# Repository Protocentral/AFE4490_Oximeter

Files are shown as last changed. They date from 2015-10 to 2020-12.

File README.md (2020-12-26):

ProtoCentral AF4490-based Pulse-oximeter shield for Arduino
================================
[Dont have it yet? Buy one here: ProtoCentral AFE4490 Pulse Oximeter Shield for Arduino – v2 (PC-MED-0406)](https://protocentral.com/product/protocentral-afe4490-pulse-oximeter-shield-for-arduino-v2/)
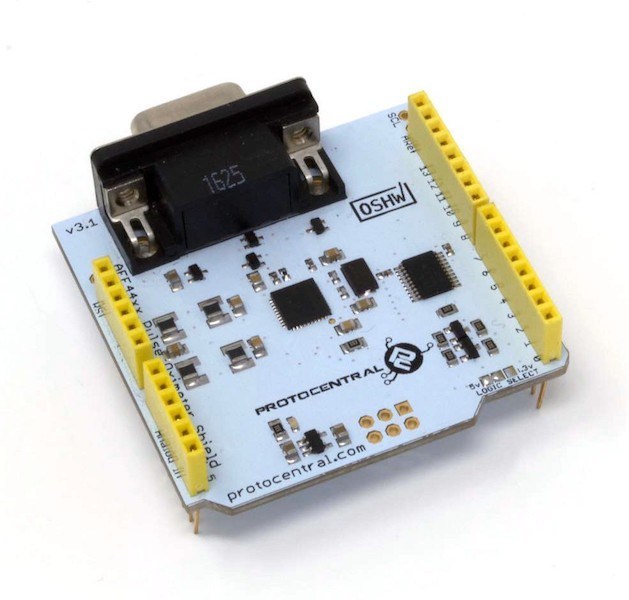
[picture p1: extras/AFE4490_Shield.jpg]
Pulse Oximeter Shield


[Dont have it yet? Buy one here: ProtoCentral AFE4490 Pulse Oximeter Breakout Board Kit (PC-MED-0405)](https://protocentral.com/product/protocentral-afe4490-pulse-oximeter-breakout-board-kit/)
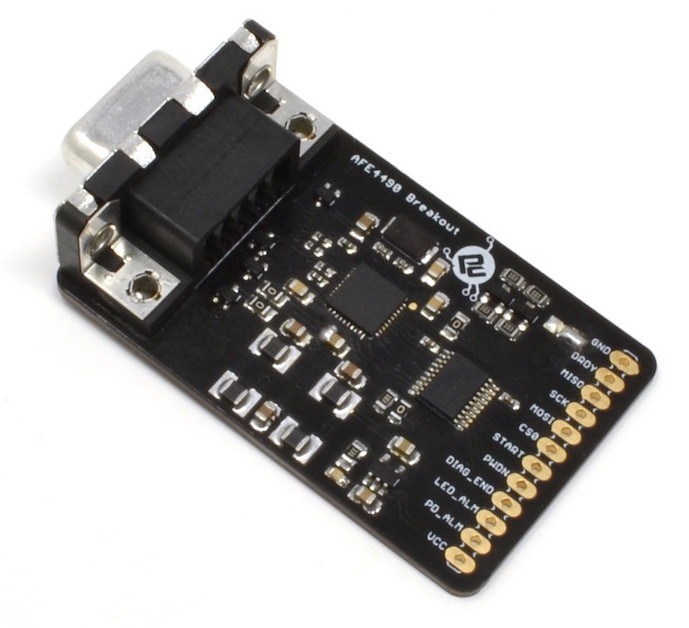
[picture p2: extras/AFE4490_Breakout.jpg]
Pulse Oximeter Breakout


### If you're looking for the Arduino library, it's now moved here: https://github.com/Protocentral/protocentral-afe4490-arduino

This pulse oximetry shield from ProtoCentral uses the AFE4490 IC to enble your Arduino to measure heart rate as well as SpO2 values.
Pulse oximetry is an indirect method of measuring the oxygen levels in the blood. The sensor measures the skin's absorbance of red and IR light wavelengths to calculate the oxygen levels. The measurement is done by a probe that clips on to a finger and contains emitters as well as a light sensor.
Since the amount of blood flowing through any blood vessel varies (pulses) with the rate of blood from the heart, this can also be used for measuring heartrate without the need for connecting any ECG electrodes. 
Used along with Brainbay, this shield can display the real-time PPG as well as heart-rate values in addition to SpO2.

Features:
* TI AFE4490 Single chip pulse pulsoximetry front-end IC
* Standard Nellcor compatible DB7 connector for probe
* Calculates Spo2 values with provided code
* Real-time display of PPG (Photoplethysmogram)

## Includes:
----------
* 1x ProtoCentral Pulse Oximetry shield for Arduino
* 1x Set of stackable Arduino headers
* 1x "Nellcor compatible" Pulse oximetry finger probe. 

## Repository Contents
-------------------
* **/arduino** - Arduino library and example sketch
* **/hardware** - All Eagle design files (.brd, .sch)
* **/extras** - datasheets and extras
* **/processing** - Processing-based Application

## Connecting the shield to your Arduino
-------------------------------------
 Connect the ECG/Respiration shield to the Arduino by stacking it on top of your Arduino. This shield uses the SPI interface  to communicate with the Arduino. Since this includes the ICSP header, which is used on newer Arduinos for SPI communication,  this shield is also compatible newer Arduino boards such as the Arduino Yun and Due.

## The Arduino library for this is now available here: https://github.com/Protocentral/protocentral-afe4490-arduino

## Wiring the Breakout to your Arduino
------------------------------------
 If you have bought the breakout the connection with the Arduino board is as follows:
 
|AFE4490 pin label| Arduino Connection   |Pin Function                  |
|----------------- |:--------------------:|-----------------:           |
| GND              | Gnd                  |  Gnd                        |             
| DRDY             | D2                   |  Data ready(interrupt)      |
| MISO             | D12                  |  Slave out                  |
| SCK              | D13                  |  SPI clock                  |
| MOSI             | D11                  |  Slave in                   |
| CS0              | D7                   |  Slave select               |
| START            | D5                   |  Conversion start Pin       |
| PWDN             | D4                   |  Power Down/ Reset          |
| DIAG_END         | NC                   |  Diagnostic output          |
| LED_ALM          | NC                   |  Cable fault indicator      |
| PD_ALM           | NC                   |  PD sensor fault indicator  |
| VCC              | +5v                  |  Supply voltage             |

## Using Processing - Data Visualization Software
----------------------------------------------
 Processing is a data visualization software, in existence since 2001, used by artists and scientists alike. It’s an open source coding framework based on Java. If you are familiar with the Arduino environment, the Processing IDE is similar and you won’t have much of a learning curve to climb!
 
 The following are the steps to run the code:

### 1. Download and Install Processing 

 Download the processing ide latest version from the link

* [Download Processing for your OS] (http://download.processing.org/)

Once downloaded, unzip the archive and install the app as per your OS.

### 2. Download the Processing code for Pulse Oximeter visualization

 a. Download the necessary files & directories or clone to your desktop from GitHub.

 b. Unzipping the archive should make a folder by name AFE4490 Oximeter Shield that contains the visualization code.

 c. Locate the Processing sketchbook directory on your computer. This should have been created automatically when you installed processing. Depending on your operating system, the path will be as follows:

* On Windows: c:/My Documents/Processing/
* On MAC: /Users/your_user_name/Documents/Processing/
* On Linux: /Home/your_user_name/sketchbook/

**Note:** This directory appears as "Processing" on Windows/Mac, and goes by the name "Sketchbook" on Linux. Create a subdirectory by name "libraries" if one doesn't exist already.

 d. From the above mentioned "AFE4490_Oximeter-master" directory Copy/Move the contents of the AFE4490_Oximeter-master/processing/openview_pulseox folder to the Processing sketchbook directory which is also mentioned above (Locate the Processing sketchbook)

 e. Finally, copy the G4P directories from AFE4490_Oximeter-master\Processing\libraries and paste them into the libraries directory of your Processing sketchbook.

 f. You are all set now to get your first PPG wave form and SpO2 reading visualized from the AFE4490 Oximeter Shield!

### 3. Uploading Arduino Sketch For AFE4490 Oximeter Shield

 a. Open the Arduino IDE to load the embedded code for AFE4490 Oximeter Shield.

 b. Click on File -> Open and Browse the .ino code for Arduino from AFE4490_Oximeter-master\arduino and export the application to Arduino.

### 4. Open Processing & launch the ces_view_oximeter

 a. If Processing IDE was open, close it and reopen to refresh the libraries and sketches. The repositories are not refreshed if the IDE was open while the Sketches and Libraries were being updated.

 b. Double-click any of the .pde files in the openview_pulseox directory to open all of the pulse oximeter code in the Processing IDE.

 c. If everything done so far was good, clicking the "run" button on the top left corner of the IDE, should run the code! If it does not, make sure you installed your libraries correctly.

 d. Once the GUI is running, select the port connect with pulse oximeter shield from the "SELECT PORT" dropdown as shown in the figure below

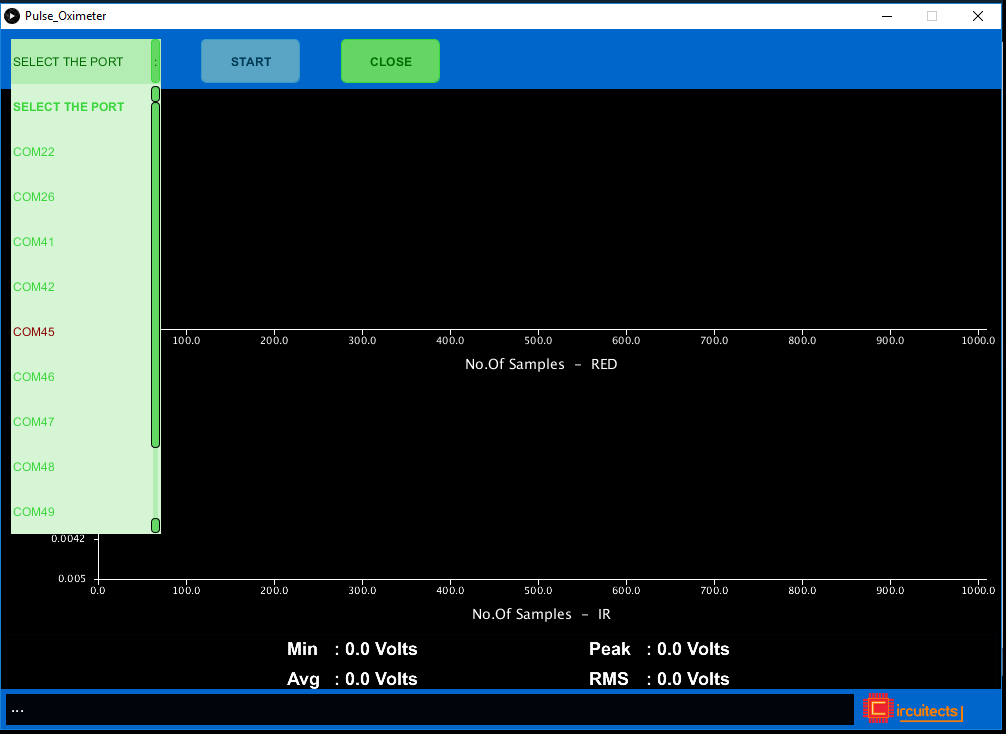
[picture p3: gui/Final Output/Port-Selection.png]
Port Selection


 e. Once the port selection is appropriate the START button gets enabled. Click "START" to initiate visualization

 f. You should see the PPG ( RED and IR) waves generated with the values obtained from the AFE4490 Oximeter Shield Breakout Board as shown below.

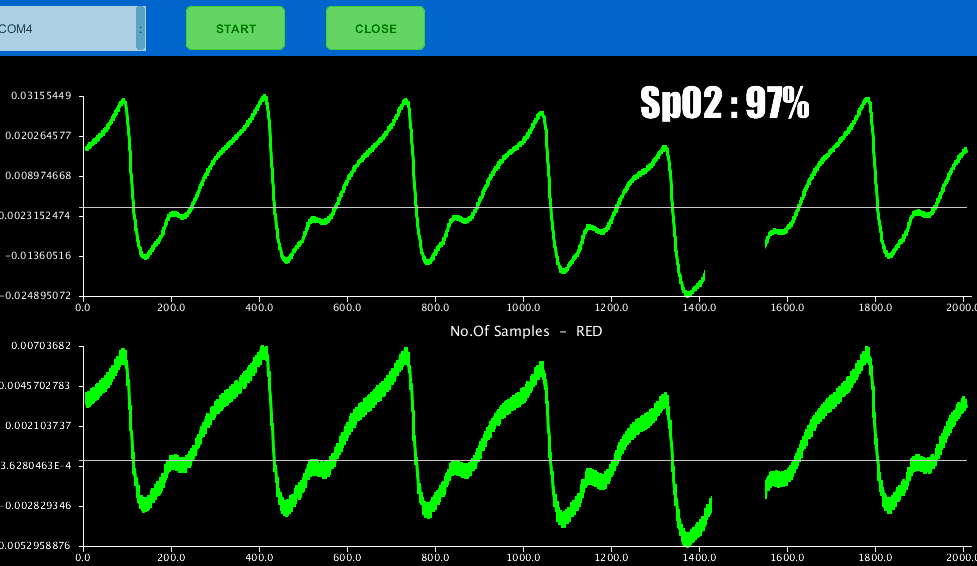
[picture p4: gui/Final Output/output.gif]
PPG Wave Form in Processing


License Information
===================

This product is open source! Both, our hardware and software are open source and licensed under the following licenses:

Hardware
---------

**All hardware is released under [Creative Commons Share-alike 4.0 International](http://creativecommons.org/licenses/by-sa/4.0/).**


You are free to:

* Share — copy and redistribute the material in any medium or format
* Adapt — remix, transform, and build upon the material for any purpose, even commercially.
The licensor cannot revoke these freedoms as long as you follow the license terms.

Under the following terms:

* Attribution — You must give appropriate credit, provide a link to the license, and indicate if changes were made. You may do so in any reasonable manner, but not in any way that suggests the licensor endorses you or your use.
* ShareAlike — If you remix, transform, or build upon the material, you must distribute your contributions under the same license as the original.

Software
--------

**All software is released under the MIT License(http://opensource.org/licenses/MIT).**

THE SOFTWARE IS PROVIDED "AS IS", WITHOUT WARRANTY OF ANY KIND, EXPRESS OR IMPLIED, INCLUDING BUT NOT LIMITED TO THE WARRANTIES OF MERCHANTABILITY, FITNESS FOR A PARTICULAR PURPOSE AND NONINFRINGEMENT. IN NO EVENT SHALL THE AUTHORS OR COPYRIGHT HOLDERS BE LIABLE FOR ANY CLAIM, DAMAGES OR OTHER LIABILITY, WHETHER IN AN ACTION OF CONTRACT, TORT OR OTHERWISE, ARISING FROM, OUT OF OR IN CONNECTION WITH THE SOFTWARE OR THE USE OR OTHER DEALINGS IN THE SOFTWARE.

Please check [*LICENSE.md*](LICENSE.md) for detailed license descriptions.

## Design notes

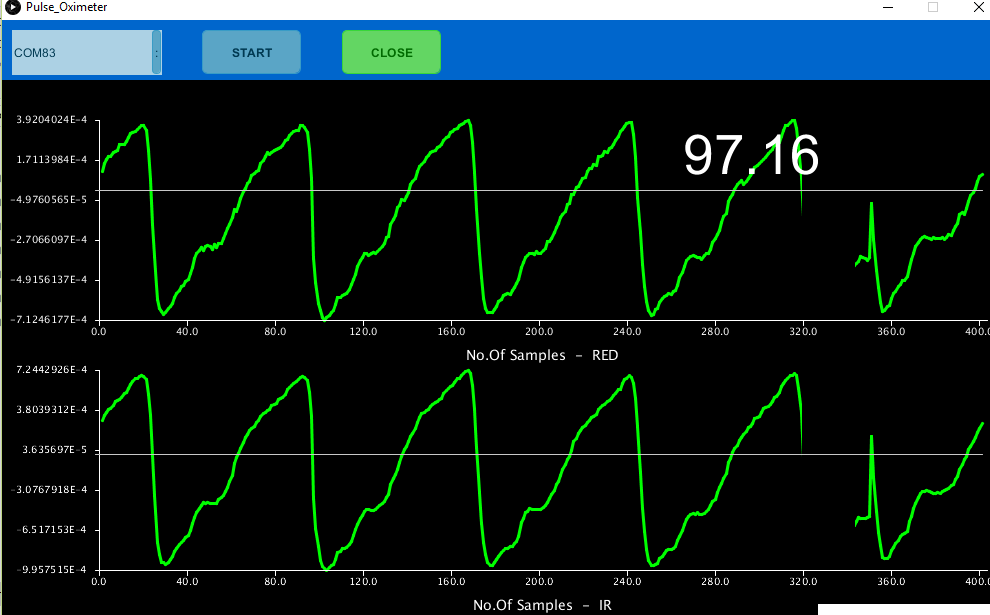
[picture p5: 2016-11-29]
gui/Final Output/output.png

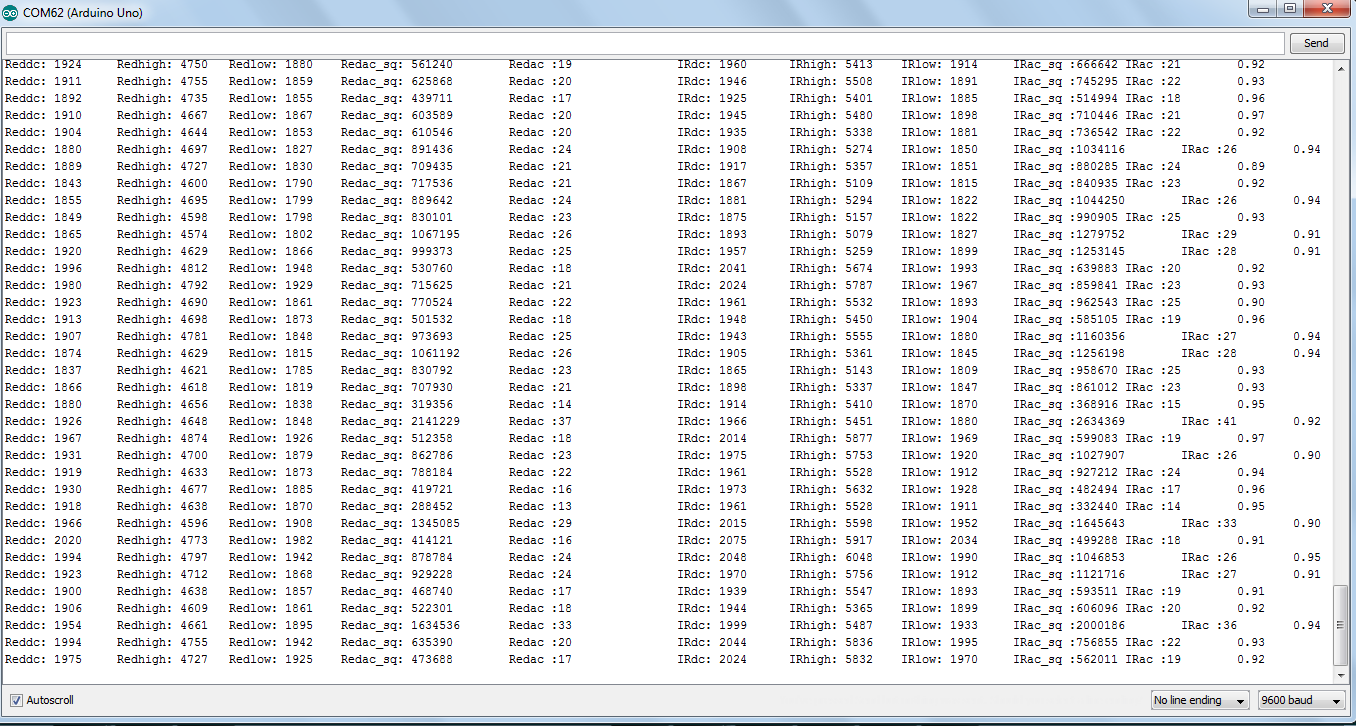
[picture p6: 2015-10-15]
extras/oximeter_serial.png

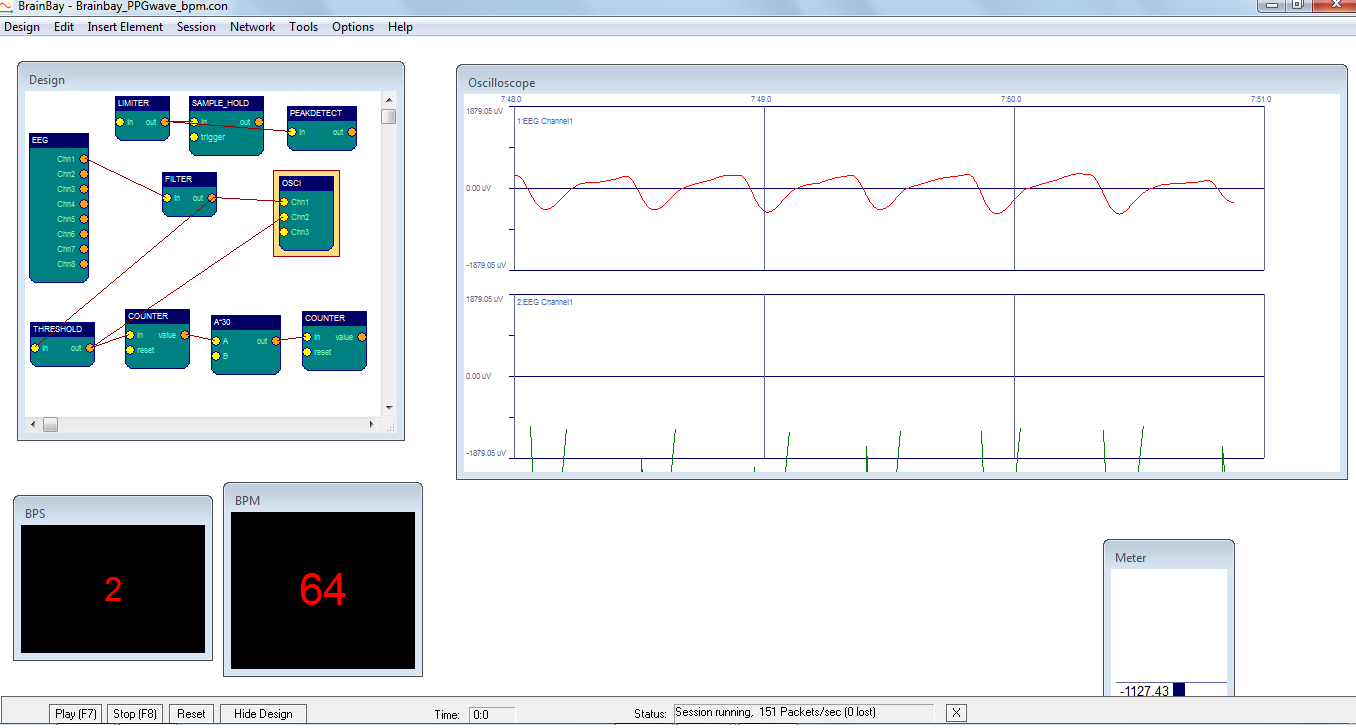
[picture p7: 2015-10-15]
extras/afe4400brainbay.png

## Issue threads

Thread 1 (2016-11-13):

### ISSUE TITLE
The polarity in D1 D2 D3 and D5 in sch is incorrect, but in pcb is correct

### ISSUE THREAD

**Issue by danieljpb** [Protocentral/AFE4490_Oximeter#1]
The polarity in D1 D2 D3 and D5 in sch is incorrect, but in brd is correct
![d1d2d3d5](https://cloud.githubusercontent.com/assets/3197644/15961771/f5e9ce84-2f06-11e6-8c4f-442bdff189f6.png)

**Comment by awhitchurch** [comment]
Yes, we are correcting this in the new version.

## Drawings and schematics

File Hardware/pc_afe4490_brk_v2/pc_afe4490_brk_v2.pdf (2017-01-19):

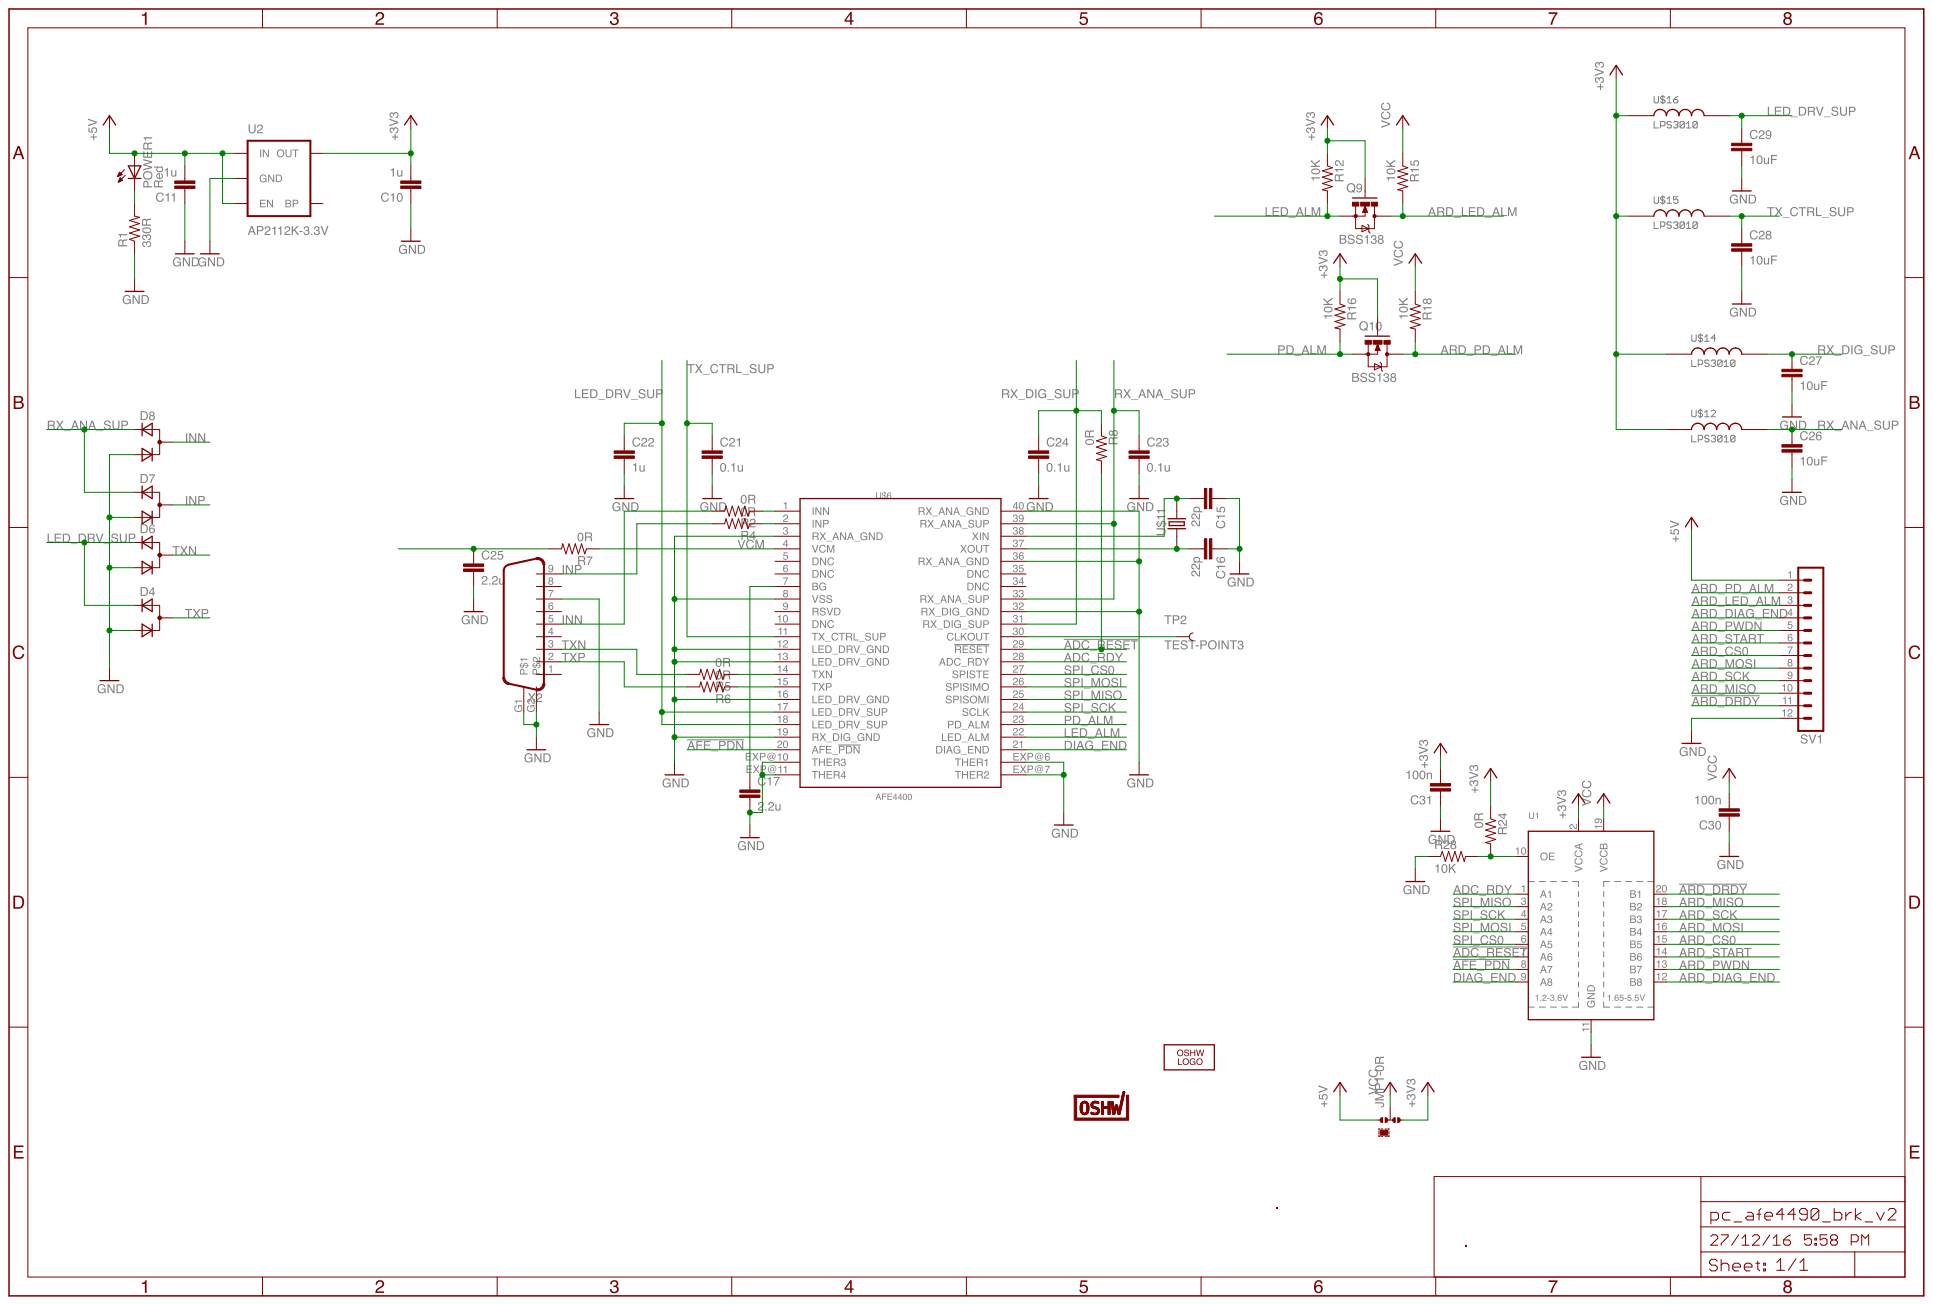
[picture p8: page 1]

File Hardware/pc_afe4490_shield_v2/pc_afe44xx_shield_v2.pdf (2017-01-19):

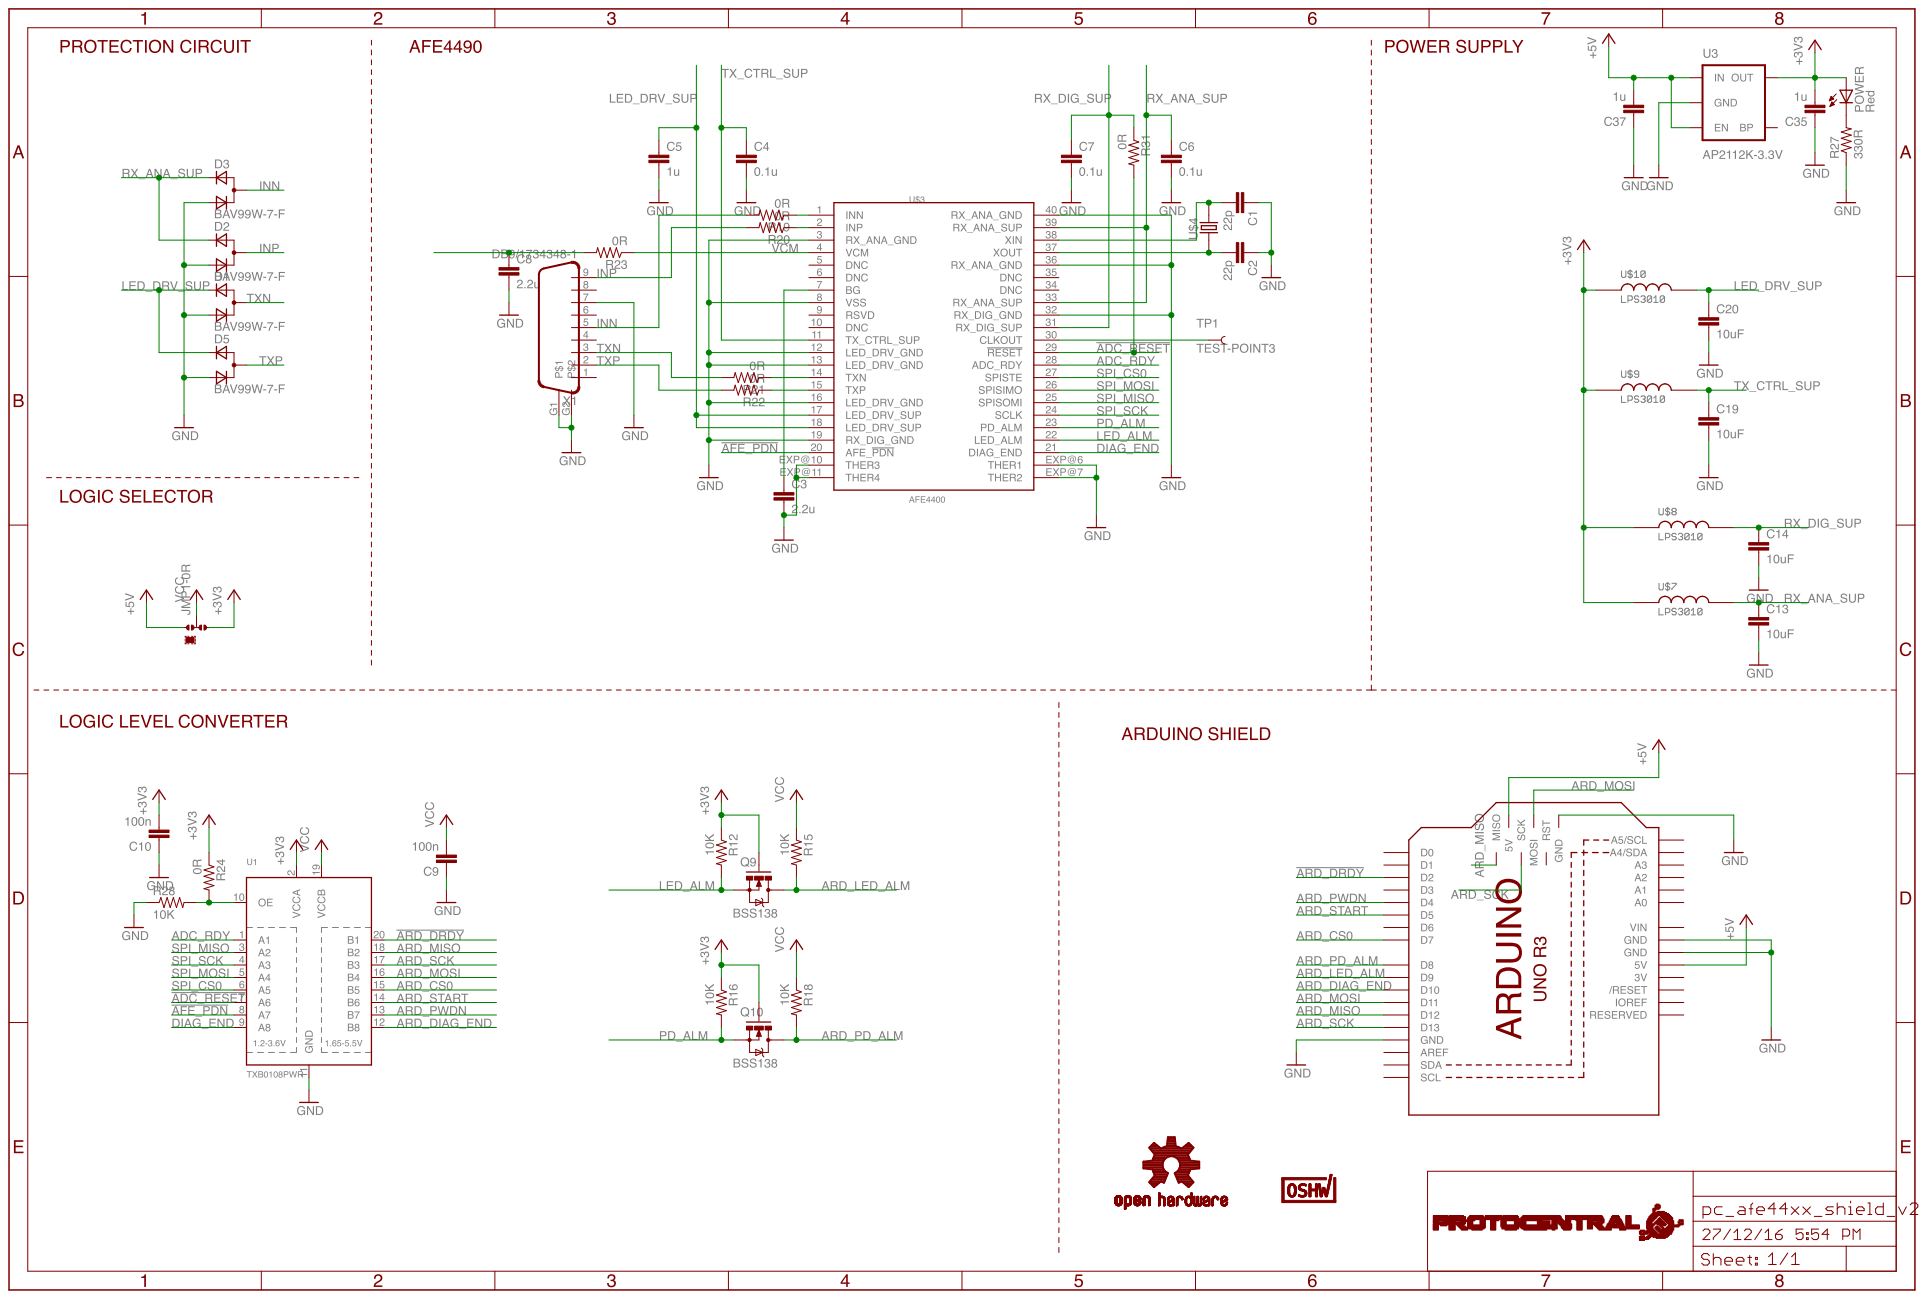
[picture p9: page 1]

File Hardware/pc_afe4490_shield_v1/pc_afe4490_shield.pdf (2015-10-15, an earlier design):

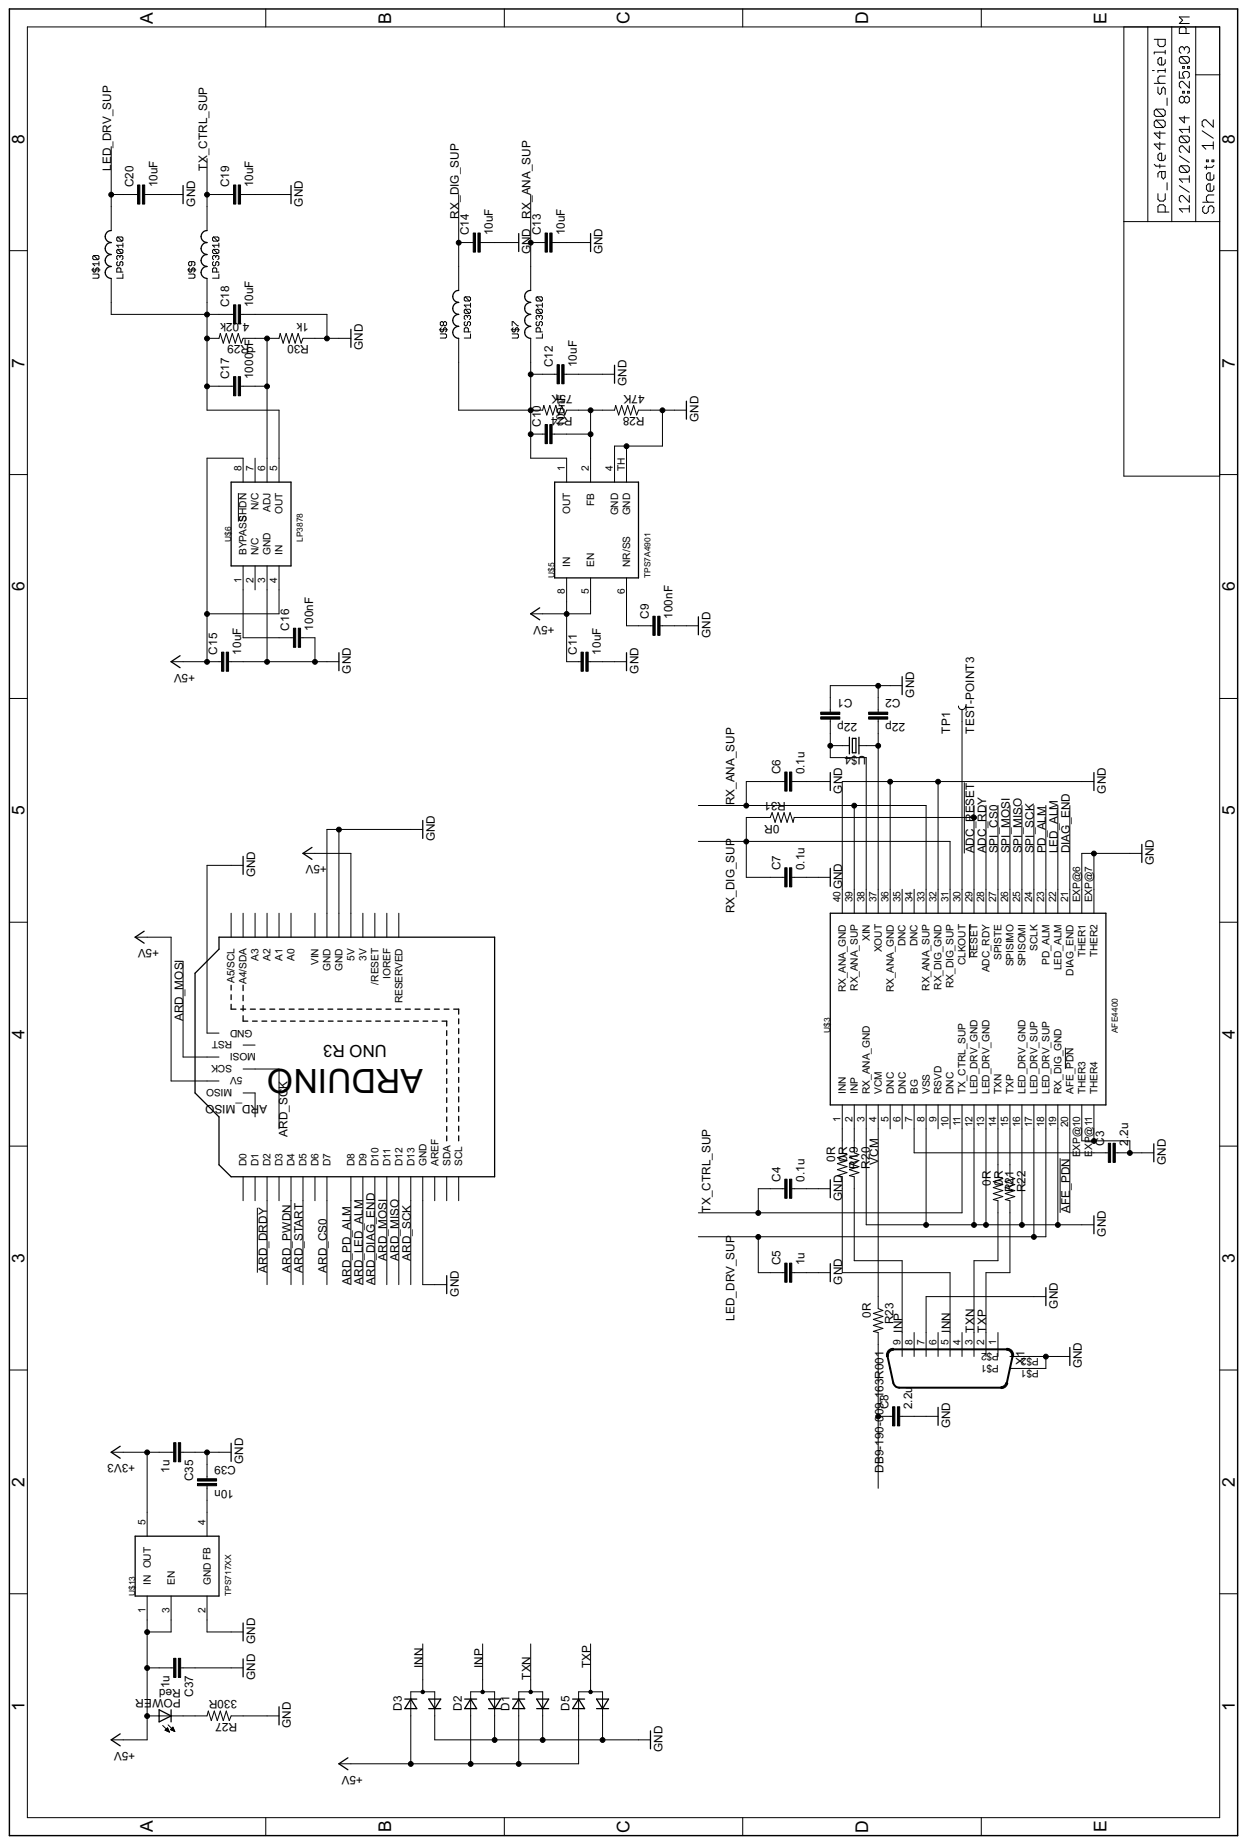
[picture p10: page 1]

GND GND V5+ GND n01 3V3+ TPS717XX GND 1u 1uGND V5+ R033 deR GND V5+ GND AFE4400 GND GND p22 p22 GND DB9-190-009-163R001 GND 2.2u GND 0.1u GND 1u GND 0.1u GND 0.1u GND GND 0R0R 0R0R 0R 2.2u GND TPS7A4901 GND 100nF GND 100nFK57 K74 GND 10uF V5+ GND LP3878 10uF 10uF 10uF GND GND 10uF GND V5+ 100nF 1000pF k20. 4 k1 GND 10uF 10uF 10uF GND GND GND V5+ GND R0 TEST-POINT3 93C U$13IN 1 EN 3 OUT 5 GND 2 FB 4 C35 C37 72R RE WOP D0D1D2D3D4D5D6D7D8D9D10 D11 D12 D13 GND AREF A5/SCL A4/SDAA3A2A1A0 VIN GND GND5V3V /RESET IOREF RESERVED SCL SDA OSI MV5 I SOM DNG KCS TSR INN 1 INP 2 RX_ANA_GND 3 VCM 4 DNC 5 DNC 6 BG 7 VSS 8 RSVD 9 DNC 10 TX_CTRL_SUP 11 LED_DRV_GND 12 LED_DRV_GND 13 TXN 14 TXP 15 LED_DRV_GND 16 LED_DRV_SUP 17 LED_DRV_SUP 18 RX_DIG_GND 19 AFE_PDN 20 DIAG_END 21 LED_ALM 22 PD_ALM 23 SCLK 24 SPISOMI 25 SPISIMO 26 SPISTE 27 ADC_RDY 28 RESET 29 CLKOUT 30 RX_DIG_SUP 31 RX_DIG_GND 32 RX_ANA_SUP 33 DNC 34 DNC 35 RX_ANA_GND 36 XOUT 37 XIN 38 RX_ANA_SUP 39 RX_ANA_GND 40 U$3 THER1 EXP@6 THER2 EXP@7 THER3 EXP@10 THER4 EXP@11 4$U 1C 2C X1 987654321 1$P 1$P 2$P 2$P C3 C4 C5 C6 C7 D5D1D2D3 R19 R20 R21 R22 R23 C8 U$5IN 8 EN 5 NR/SS 6 OUT 1 FB 2 GND 4 GND TH C9 C1042R 82R C11 BYPASS 1 N/C 2 GND 3 IN 4 OUT 5 ADJ 6 N/C 7 SHDN 8 U$6 C12 C13 C14 C15 C16 C17 92R 03R C18 C19 C20 13R TP1 SPI_MISO SPI_SCK SPI_MOSI SPI_CS0 ARD_MOSI ARD_MOSI ARD_MISO OSI M_DRA ARD_SCK ARD_SCK ARD_CS0 ARD_DRDY ARD_START ARD_PWDN ADC_RDY ADC_RESET AFE_PDN DIAG_END PD_ALM LED_ALM INN INN INP INP TXN TXN TXP TXP VCM ARD_PD_ALM ARD_LED_ALM ARD_DIAG_END RX_ANA_SUP RX_ANA_SUP LED_DRV_SUP LED_DRV_SUP TX_CTRL_SUP TX_CTRL_SUP RX_DIG_SUP RX_DIG_SUP ONI UDRA 3R ONU ABCDE 1 2 3 4 5 6 7 8 ABCDE 1 2 3 4 5 6 7 8

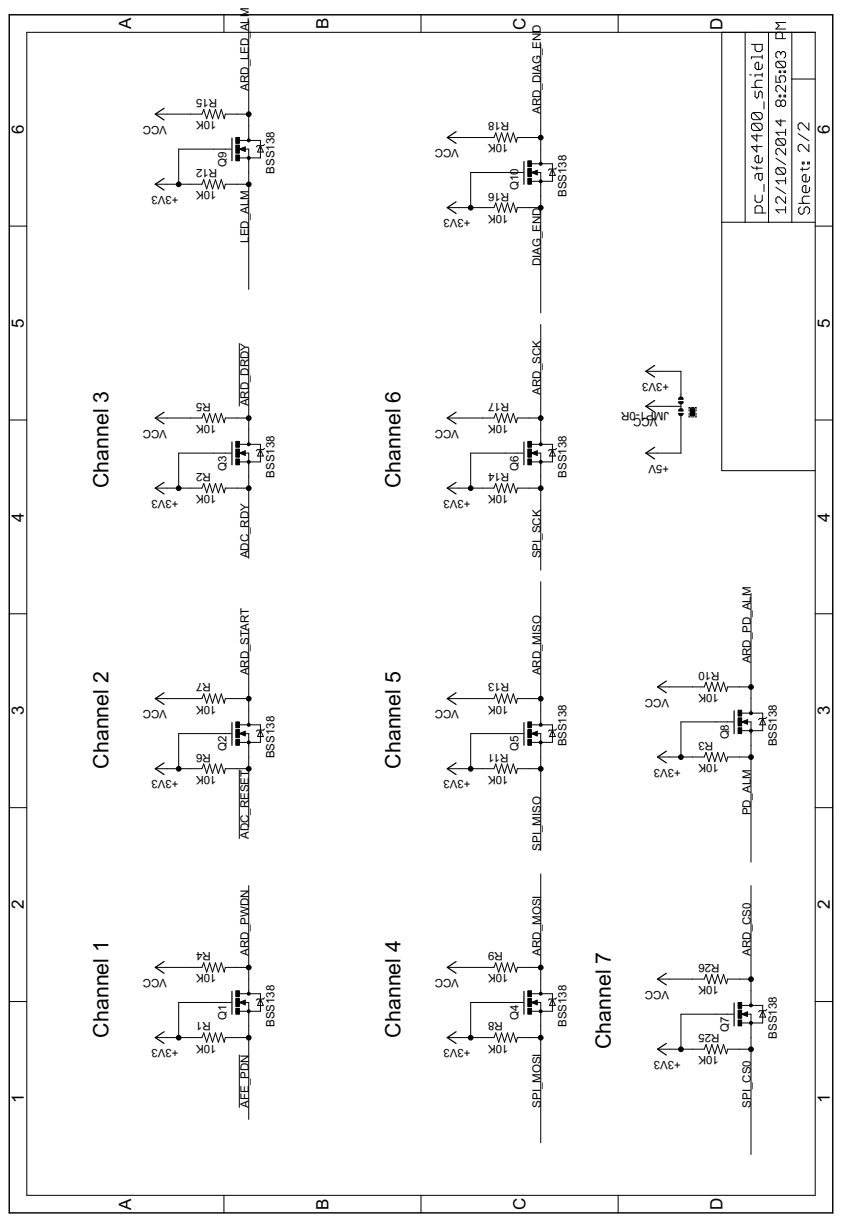
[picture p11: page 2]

BSS138 K01 K01 BSS138 K01 K01 BSS138 K01 K01 BSS138 K01 K01 BSS138 K01 K01 BSS138 K01 K01 BSS138 K01 K01 3V3+ 3V3+ 3V3+ 3V3+ 3V3+ 3V3+ 3V3+ BSS138 K01 K01 3V3+ BSS138 K01 K01 3V3+ BSS138 K01 K01 3V3+ V5+ 3V3+ CCV CCV CCV CCV CCV CCV CCV CCV CCV CCV CCV Channel 1 Channel 2 Channel 3 Channel 4 Channel 5 Channel 6 Channel 7 Q1 1R4R Q2 6R7R Q3 2R5R Q4 8R9R Q5 11R 31RQ6 41R 71R Q7 52R 62RQ8 3R01R Q9 21R 51R Q10 61R 81R R0- 1P MJ ARD_CS0 SPI_CS0 AFE_PDN ARD_PWDN ADC_RESET ARD_START ADC_RDY ARD_DRDY SPI_MOSI ARD_MOSI SPI_MISO ARD_MISO SPI_SCK ARD_SCK PD_ALM ARD_PD_ALM LED_ALM ARD_LED_ALM DIAG_END ARD_DIAG_END ABCD 1 2 3 4 5 6 ABCD 1 2 3 4 5 6

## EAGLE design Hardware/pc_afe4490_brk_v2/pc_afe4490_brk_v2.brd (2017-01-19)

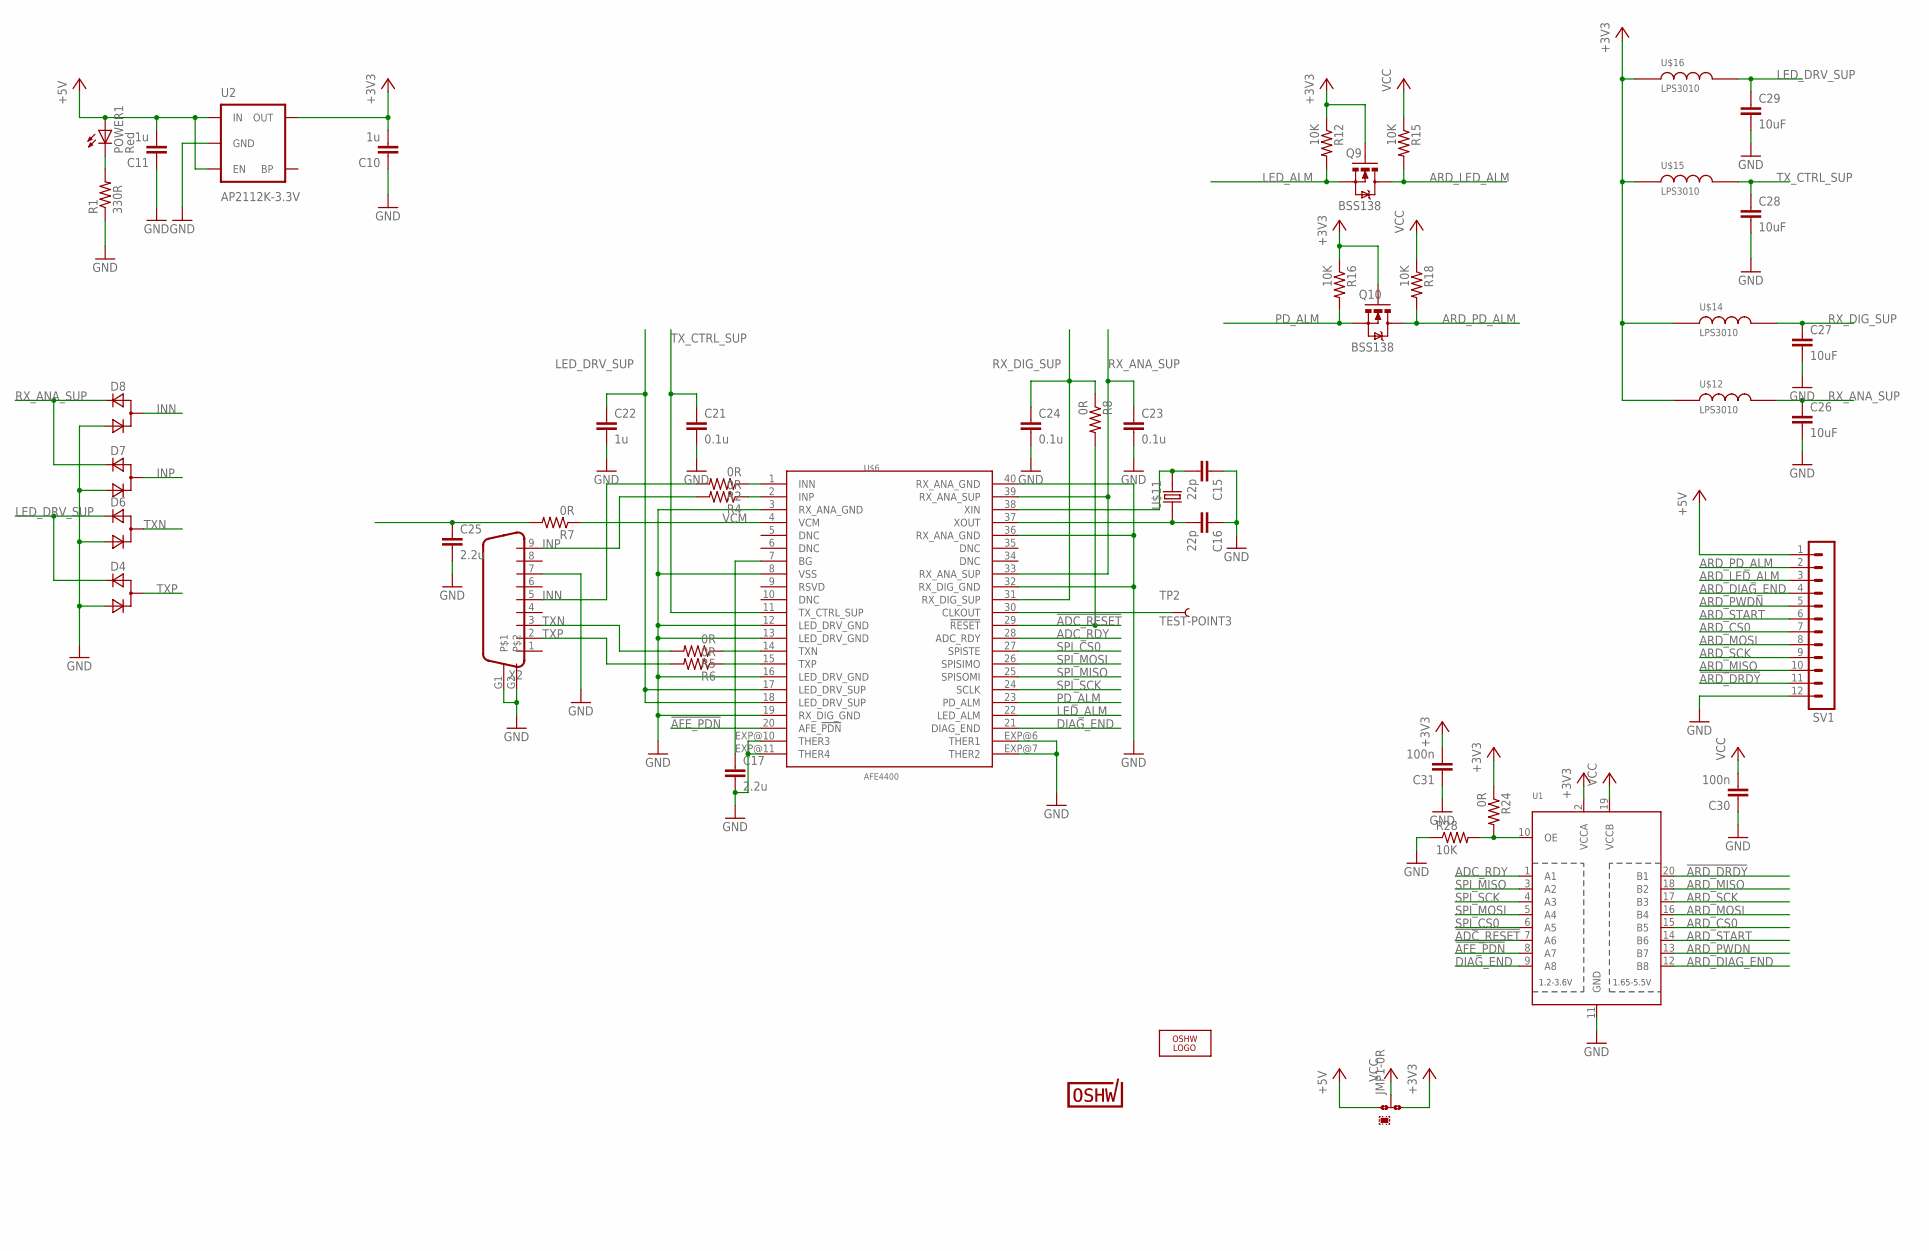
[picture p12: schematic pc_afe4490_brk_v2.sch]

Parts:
C10, C11, C22: 1u; C0805
C15, C16: 22p; C0402
C17, C25: 2.2u; C0402
C21, C23, C24: 0.1u; C0805
C26, C27, C28, C29: 10uF; C0805
C30, C31: 100n; C0402
D4, D6, D7, D8: D_ACACSOT323; SOT323
JMP1: 0R-JUMPA; A0R-JMP
LOGO2: OSHW_LOGO_FILLX0200-NT; OSHW_FILLX200_NOTEXT
POWER1: Red; CHIPLED_0603
Q9, Q10: BSS138; SOT23-3
R1: 330R; R0805
R2, R4, R7: 0R; R0402
R5, R6, R8: 0R; R0805
R12, R15, R16, R18, R28: 10K; 0805
R24: 0R; 0805
SV1: MA12-1
TP2: TEST-POINT3; PAD.03X.03
U1: TXB0108PWR; TSSOP20
U2: AP2112K-3.3V; SOT23-5
U$1: PROTY-LOGO; LOGO-PROTY
U$3: PROTY_LOGO_WITH_TEXT; PROTY_WITH_TEXT
U$4: CERT-SMALL; CERT-SMALL-SILK
U$6: AFE4400; QFN-40
U$11: ABM3
U$12, U$14, U$15, U$16: LPS3010; LPS
X2: DB9

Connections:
!ADC_RESET: R8.2, U1.7 (A6), U$6.29 (!RESET)
!AFE_PDN: U1.8 (A7), U$6.20 (AFE_!PDN)
!ARD_DRDY: SV1.11, U1.20 (B1)
+3V3: C10.2, C31.2, JMP1.3, Q9.1 (G), Q10.1 (G), R12.1, R16.1, R24.1, U1.2 (VCCA), U2.5 (OUT), U$12.1, U$14.1, U$15.1, U$16.1
+5V: C11.2, JMP1.1, POWER1.A, SV1.1, U2.1 (IN), U2.3 (EN)
ADC_RDY: U1.1 (A1), U$6.28 (ADC_RDY)
ARD_CS0: SV1.7, U1.15 (B5)
ARD_DIAG_END: SV1.4, U1.12 (B8)
ARD_LED_ALM: Q9.3 (D), R15.2, SV1.3
ARD_MISO: SV1.10, U1.18 (B2)
ARD_MOSI: SV1.8, U1.16 (B4)
ARD_PD_ALM: Q10.3 (D), R18.2, SV1.2
ARD_PWDN: SV1.5, U1.13 (B7)
ARD_SCK: SV1.9, U1.17 (B3)
ARD_START: SV1.6, U1.14 (B6)
DIAG_END: U1.9 (A8), U$6.21 (DIAG_END)
GND: C10.1, C11.1, C15.1, C16.1, C17.2, C21.2, C22.2, C23.2, C24.2, C25.2, C26.2, C27.2, C28.2, C29.2, C30.1, C31.1, D4.2 (C), D6.2 (C), D7.2 (C), D8.2 (C), R1.1, R28.1, SV1.12, U1.11 (GND), U2.2 (GND), U$6.3 (RX_ANA_GND), U$6.8 (VSS), U$6.12 (LED_DRV_GND), U$6.13 (LED_DRV_GND), U$6.16 (LED_DRV_GND), U$6.19 (RX_DIG_GND), U$6.32 (RX_DIG_GND), U$6.36 (RX_ANA_GND), U$6.40 (RX_ANA_GND), U$6.EXP@6 (THER1), U$6.EXP@7 (THER2), U$6.EXP@10 (THER3), U$6.EXP@11 (THER4), X2.7, X2.G1, X2.G2
INN: D8.1 (CA), R2.2, X2.5
INP: D7.1 (CA), R4.2, X2.9
LED_ALM: Q9.2 (S), R12.2, U$6.22 (LED_ALM)
LED_DRV_SUP: C22.1, C29.1, D4.3 (A), D6.3 (A), U$6.17 (LED_DRV_SUP), U$6.18 (LED_DRV_SUP), U$16.2
unnamed: POWER1.C, R1.2
unnamed: C15.2, U$6.38 (XIN), U$11.2
unnamed: C16.2, U$6.37 (XOUT), U$11.1
unnamed: C17.1, U$6.7 (BG)
unnamed: TP2.P$1, U$6.30 (CLKOUT)
unnamed: R2.1, U$6.1 (INN)
unnamed: R4.1, U$6.2 (INP)
unnamed: R5.1, U$6.14 (TXN)
unnamed: R6.1, U$6.15 (TXP)
unnamed: C25.1, R7.2
OE: R24.2, R28.2, U1.10 (OE)
PD_ALM: Q10.2 (S), R16.2, U$6.23 (PD_ALM)
RX_ANA_SUP: C23.1, C26.1, D7.3 (A), D8.3 (A), U$6.33 (RX_ANA_SUP), U$6.39 (RX_ANA_SUP), U$12.2
RX_DIG_SUP: C24.1, C27.1, R8.1, U$6.31 (RX_DIG_SUP), U$14.2
SPI_CS0: U1.6 (A5), U$6.27 (SPISTE)
SPI_MISO: U1.3 (A2), U$6.25 (SPISOMI)
SPI_MOSI: U1.5 (A4), U$6.26 (SPISIMO)
SPI_SCK: U1.4 (A3), U$6.24 (SCLK)
TXN: D6.1 (CA), R5.2, X2.3
TXP: D4.1 (CA), R6.2, X2.2
TX_CTRL_SUP: C21.1, C28.1, U$6.11 (TX_CTRL_SUP), U$15.2
VCC: C30.2, JMP1.2, R15.1, R18.1, U1.19 (VCCB)
VCM: R7.1, U$6.4 (VCM)

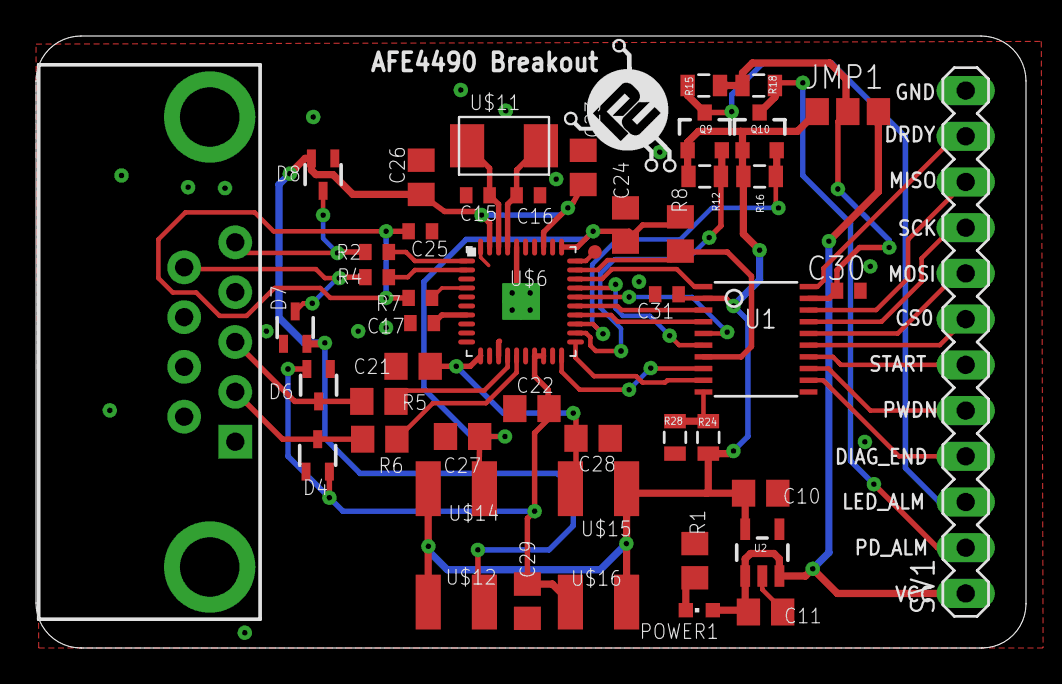
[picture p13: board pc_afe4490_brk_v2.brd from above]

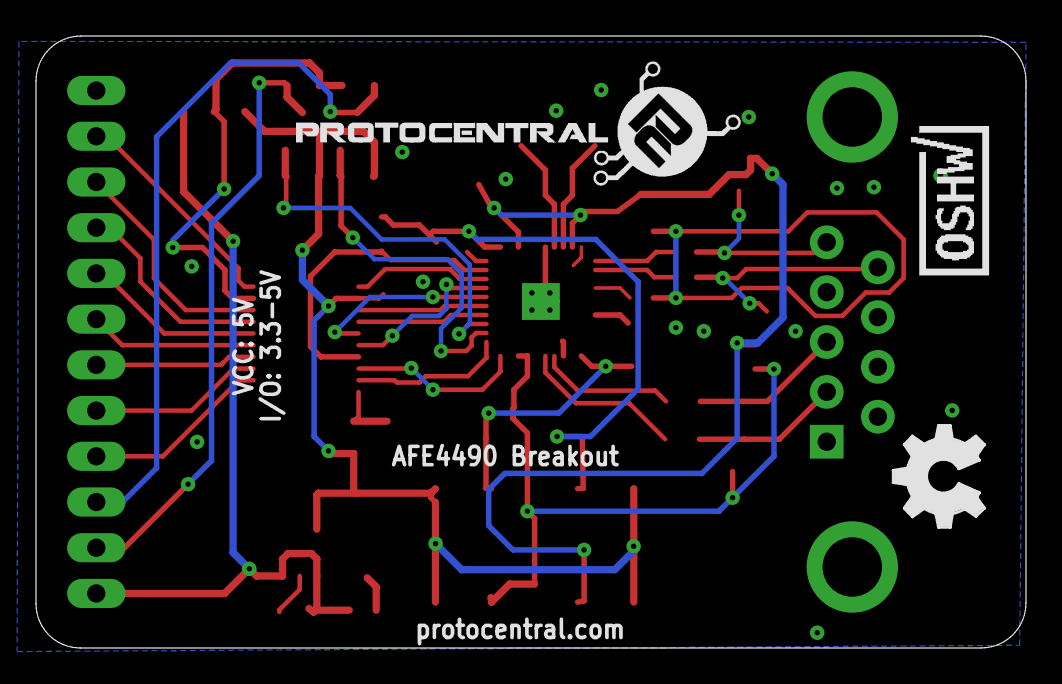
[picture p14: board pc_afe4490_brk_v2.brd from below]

Board: 4 copper layers, 55.0 x 34.0 mm, 52 parts (3 on the bottom side), 44 nets.

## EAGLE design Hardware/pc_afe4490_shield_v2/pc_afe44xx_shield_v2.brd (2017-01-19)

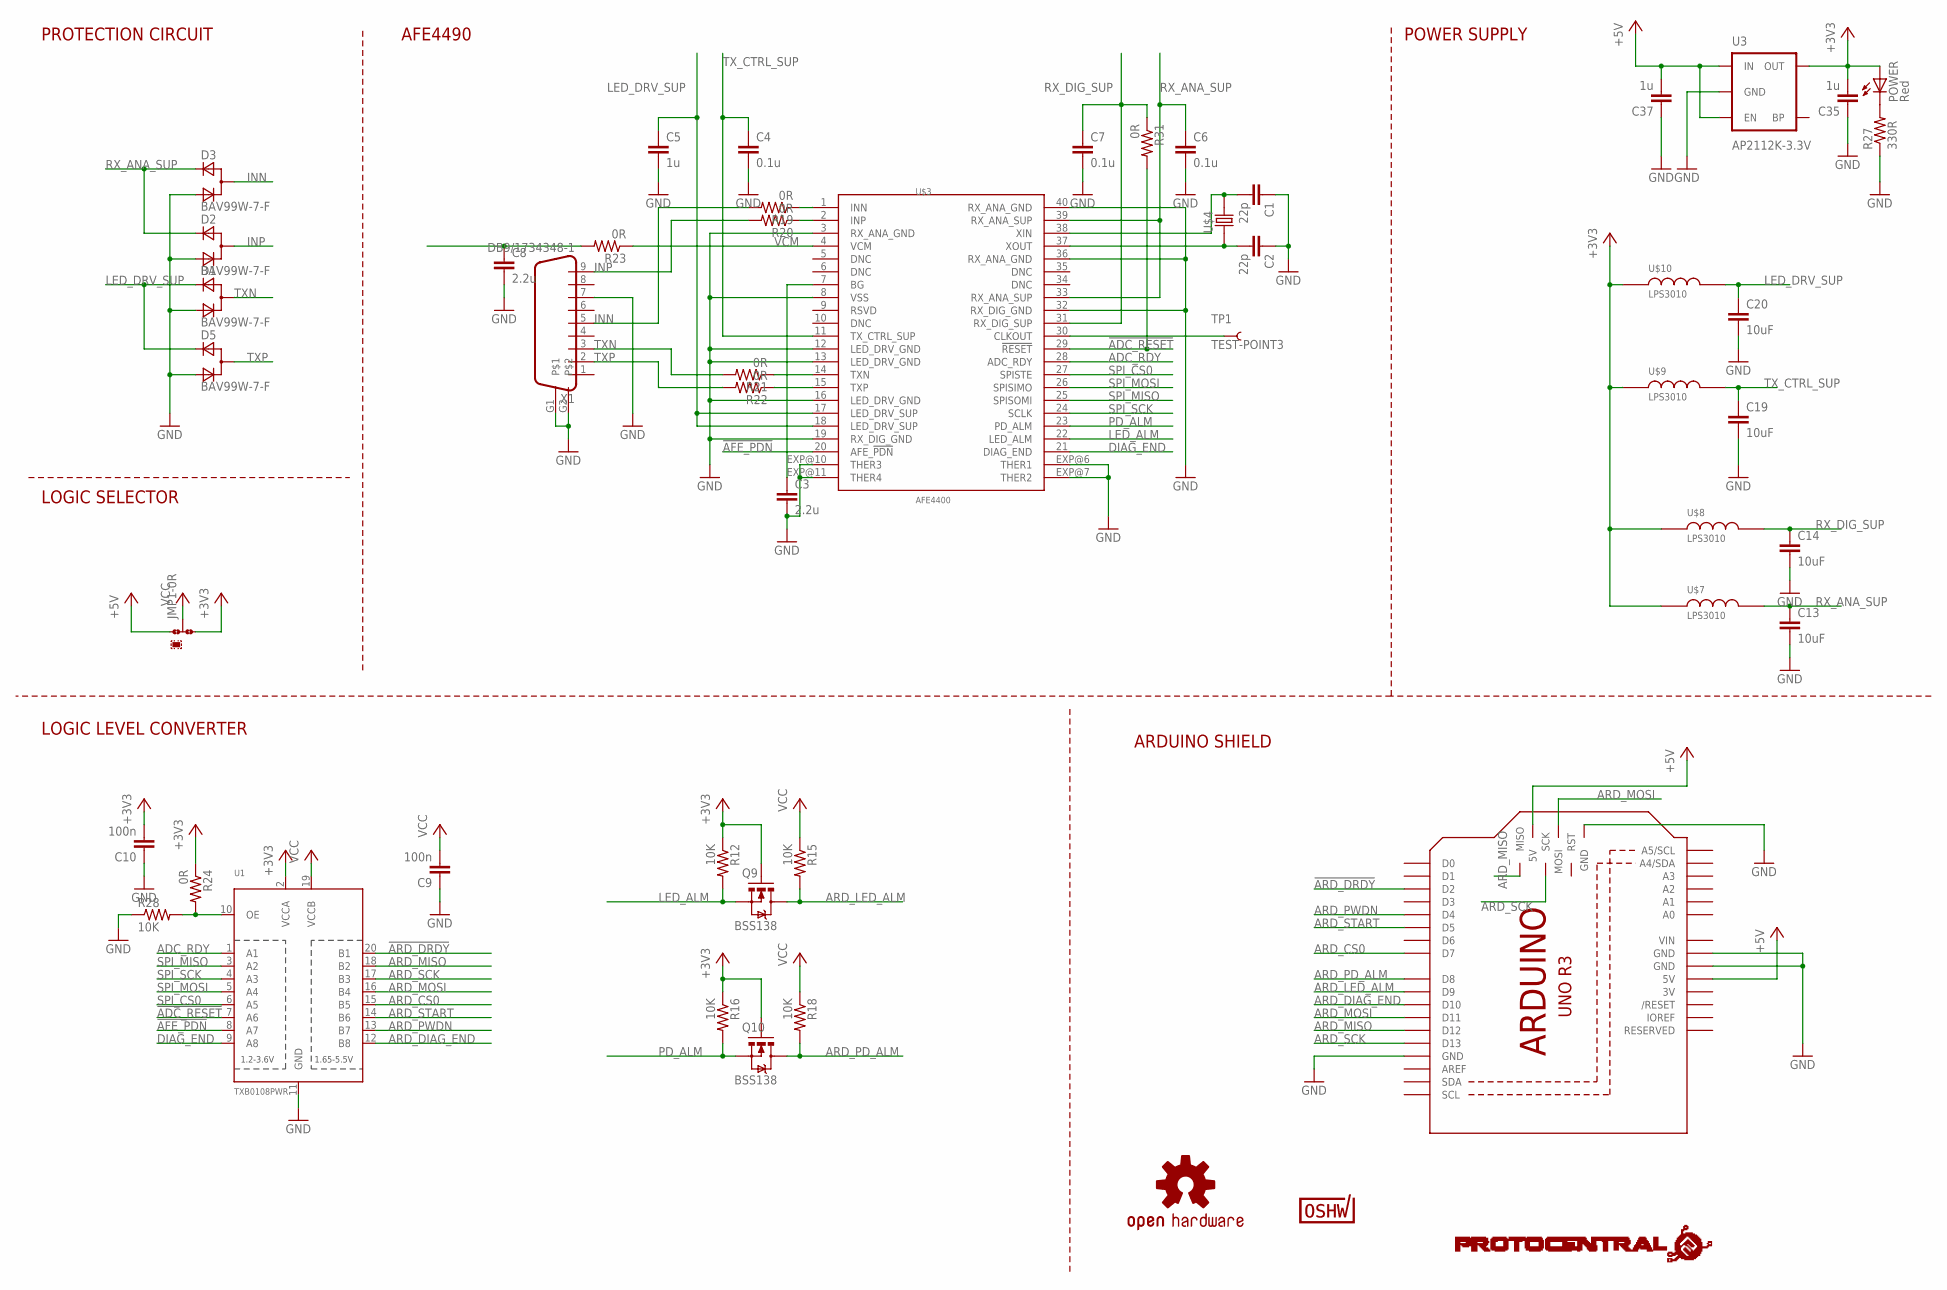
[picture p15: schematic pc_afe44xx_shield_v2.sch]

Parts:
C1, C2: 22p; C0402
C3, C8: 2.2u; C0402
C4, C6, C7: 0.1u; C0805
C5, C35, C37: 1u; C0805
C9, C10: 100n; C0402
C13, C14, C19, C20: 10uF; C0805
D1, D2, D3, D5: BAV99W-7-F; SOT323
JMP1: 0R-JUMPA; A0R-JMP
M1: ARDUINO
POWER: Red; CHIPLED_0603
Q9, Q10: BSS138; SOT23-3
R12, R15, R16, R18, R28: 10K; 0805
R19, R20, R23: 0R; R0402
R21, R22, R31: 0R; R0805
R24: 0R; 0805
R27: 330R; R0805
TP1: TEST-POINT3; PAD.03X.03
U1: TXB0108PWR; TSSOP20
U3: AP2112K-3.3V; SOT23-5
U$3: AFE4400; QFN-40
U$4: ABM3
U$5: PROTY_LOGO_WITH_TEXT; PROTY_WITH_TEXT
U$6: CERT-SMALL; CERT-SMALL-SILK
U$7, U$8, U$9, U$10: LPS3010; LPS
U$11: OSHW-LOGOM; OSHW-LOGO-M
X1: DB9/1734348-1; DB9

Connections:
3V: M1.3V
!ADC_RESET: R31.2, U1.7 (A6), U$3.29 (!RESET)
!AFE_PDN: U1.8 (A7), U$3.20 (AFE_!PDN)
!ARD_DRDY: M1.D2, U1.20 (B1)
+3V3: C10.2, C35.2, JMP1.3, POWER.A, Q9.1 (G), Q10.1 (G), R12.1, R16.1, R24.1, U1.2 (VCCA), U3.5 (OUT), U$7.1, U$8.1, U$9.1, U$10.1
+5V: C37.2, JMP1.1, M1.5V, M1.5V_ICSP (5V), U3.1 (IN), U3.3 (EN)
ADC_RDY: U1.1 (A1), U$3.28 (ADC_RDY)
ARD_CS0: M1.D7, U1.15 (B5)
ARD_DIAG_END: M1.D10, U1.12 (B8)
ARD_LED_ALM: M1.D9, Q9.3 (D), R15.2
ARD_MISO: M1.D12, M1.MISO, U1.18 (B2)
ARD_MOSI: M1.D11, M1.MOSI, U1.16 (B4)
ARD_PD_ALM: M1.D8, Q10.3 (D), R18.2
ARD_PWDN: M1.D4, U1.13 (B7)
ARD_SCK: M1.D13, M1.SCK, U1.17 (B3)
ARD_START: M1.D5, U1.14 (B6)
DIAG_END: U1.9 (A8), U$3.21 (DIAG_END)
GND: C1.1, C2.1, C3.2, C4.2, C5.2, C6.2, C7.2, C8.2, C9.1, C10.1, C13.2, C14.2, C19.2, C20.2, C35.1, C37.1, D1.2 (C), D2.2 (C), D3.2 (C), D5.2 (C), M1.GND, M1.GND@1 (GND), M1.GND@2 (GND), M1.GND@3 (GND), R27.1, R28.1, U1.11 (GND), U3.2 (GND), U$3.3 (RX_ANA_GND), U$3.8 (VSS), U$3.12 (LED_DRV_GND), U$3.13 (LED_DRV_GND), U$3.16 (LED_DRV_GND), U$3.19 (RX_DIG_GND), U$3.32 (RX_DIG_GND), U$3.36 (RX_ANA_GND), U$3.40 (RX_ANA_GND), U$3.EXP@6 (THER1), U$3.EXP@7 (THER2), U$3.EXP@10 (THER3), U$3.EXP@11 (THER4), X1.7, X1.G1, X1.G2
INN: D3.1 (CA), R19.2, X1.5
INP: D2.1 (CA), R20.2, X1.9
LED_ALM: Q9.2 (S), R12.2, U$3.22 (LED_ALM)
LED_DRV_SUP: C5.1, C20.1, D1.3 (A), D5.3 (A), U$3.17 (LED_DRV_SUP), U$3.18 (LED_DRV_SUP), U$10.2
unnamed: C3.1, U$3.7 (BG)
unnamed: R21.1, U$3.14 (TXN)
unnamed: TP1.P$1, U$3.30 (CLKOUT)
unnamed: R22.1, U$3.15 (TXP)
unnamed: POWER.C, R27.2
unnamed: R19.1, U$3.1 (INN)
unnamed: C8.1, R23.2
unnamed: C1.2, U$3.38 (XIN), U$4.2
unnamed: C2.2, U$3.37 (XOUT), U$4.1
unnamed: R24.2, R28.2, U1.10 (OE)
unnamed: R20.1, U$3.2 (INP)
PD_ALM: Q10.2 (S), R16.2, U$3.23 (PD_ALM)
RX_ANA_SUP: C6.1, C13.1, D2.3 (A), D3.3 (A), U$3.33 (RX_ANA_SUP), U$3.39 (RX_ANA_SUP), U$7.2
RX_DIG_SUP: C7.1, C14.1, R31.1, U$3.31 (RX_DIG_SUP), U$8.2
SPI_CS0: U1.6 (A5), U$3.27 (SPISTE)
SPI_MISO: U1.3 (A2), U$3.25 (SPISOMI)
SPI_MOSI: U1.5 (A4), U$3.26 (SPISIMO)
SPI_SCK: U1.4 (A3), U$3.24 (SCLK)
TXN: D1.1 (CA), R21.2, X1.3
TXP: D5.1 (CA), R22.2, X1.2
TX_CTRL_SUP: C4.1, C19.1, U$3.11 (TX_CTRL_SUP), U$9.2
VCC: C9.2, JMP1.2, R15.1, R18.1, U1.19 (VCCB)
VCM: R23.1, U$3.4 (VCM)
VIN: M1.VIN

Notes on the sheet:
POWER SUPPLY
ARDUINO SHIELD
LOGIC LEVEL CONVERTER
LOGIC SELECTOR
PROTECTION CIRCUIT
AFE4490

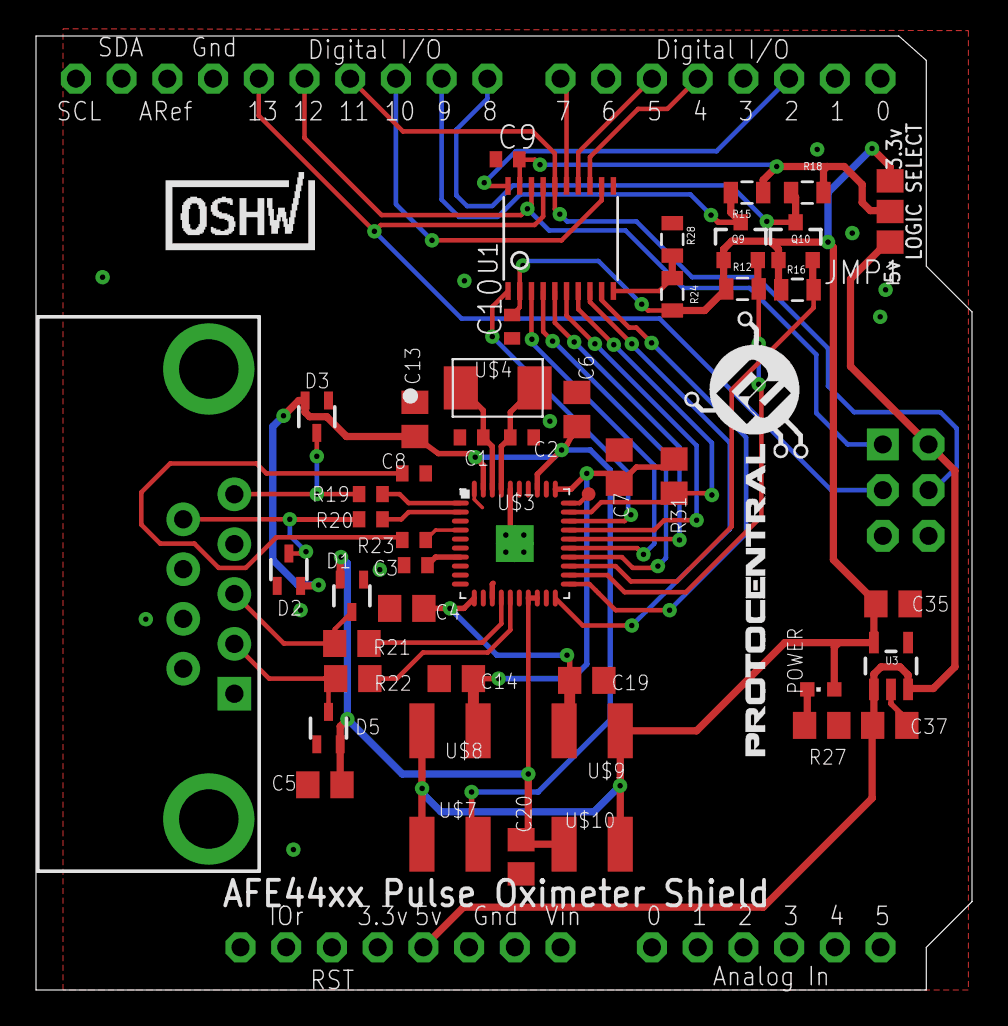
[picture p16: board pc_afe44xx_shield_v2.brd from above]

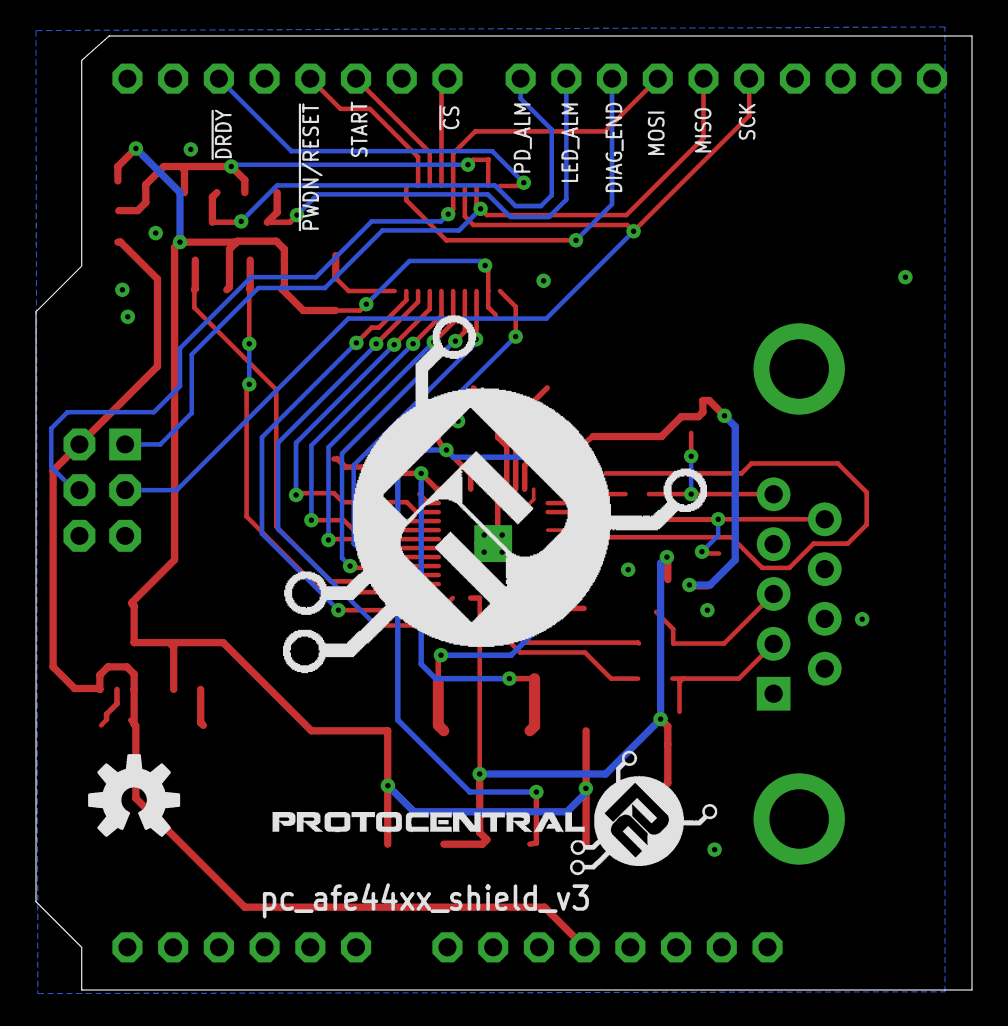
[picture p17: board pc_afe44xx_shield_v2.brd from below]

Board: 4 copper layers, 52.0 x 53.0 mm, 53 parts (3 on the bottom side), 44 nets.

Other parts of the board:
U$1: PROTY_WITH_TEXT
U$2: PROTY-LOGO-LARGE

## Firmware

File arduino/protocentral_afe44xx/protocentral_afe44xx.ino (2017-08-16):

//////////////////////////////////////////////////////////////////////////////////////////
//
//   AFE44xx Arduino Firmware
//
//   Copyright (c) 2016 ProtoCentral
//   
//   SpO2 computation based on original code from Maxim Integrated 
//
//   This software is licensed under the MIT License(http://opensource.org/licenses/MIT). 
//   
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
//   For information on how to use the HealthyPi, visit https://github.com/Protocentral/afe44xx_Oximeter
/////////////////////////////////////////////////////////////////////////////////////////

#include <string.h>
#include <SPI.h>
#include <math.h>

//afe44xx Register definition
#define CONTROL0    0x00
#define LED2STC     0x01
#define LED2ENDC    0x02
#define LED2LEDSTC    0x03
#define LED2LEDENDC   0x04
#define ALED2STC    0x05
#define ALED2ENDC   0x06
#define LED1STC     0x07
#define LED1ENDC    0x08
#define LED1LEDSTC    0x09
#define LED1LEDENDC   0x0a
#define ALED1STC    0x0b
#define ALED1ENDC   0x0c
#define LED2CONVST    0x0d
#define LED2CONVEND   0x0e
#define ALED2CONVST   0x0f
#define ALED2CONVEND  0x10
#define LED1CONVST    0x11
#define LED1CONVEND   0x12
#define ALED1CONVST   0x13
#define ALED1CONVEND  0x14
#define ADCRSTCNT0    0x15
#define ADCRSTENDCT0  0x16
#define ADCRSTCNT1    0x17
#define ADCRSTENDCT1  0x18
#define ADCRSTCNT2    0x19
#define ADCRSTENDCT2  0x1a
#define ADCRSTCNT3    0x1b
#define ADCRSTENDCT3  0x1c
#define PRPCOUNT    0x1d
#define CONTROL1    0x1e
#define SPARE1      0x1f
#define TIAGAIN     0x20
#define TIA_AMB_GAIN  0x21
#define LEDCNTRL    0x22
#define CONTROL2    0x23
#define SPARE2      0x24
#define SPARE3      0x25
#define SPARE4      0x26
#define SPARE4      0x26
#define RESERVED1   0x27
#define RESERVED2   0x28
#define ALARM     0x29
#define LED2VAL     0x2a
#define ALED2VAL    0x2b
#define LED1VAL     0x2c
#define ALED1VAL    0x2d
#define LED2ABSVAL    0x2e
#define LED1ABSVAL    0x2f
#define DIAG      0x30
#define count 60

#define CES_CMDIF_PKT_START_1   0x0A
#define CES_CMDIF_PKT_START_2   0xFA
#define CES_CMDIF_TYPE_DATA   0x02
#define CES_CMDIF_PKT_STOP    0x0B


//int IRheartsignal[count];
//int Redheartsignal[count];
int IRdc[count];
int Reddc[count];
double difIRheartsig_dc;
double difREDheartsig_dc;
double powdifIR;
double powdifRed;
double IRac; 
double Redac;
double SpOpercentage;
double Ratio;

const int SOMI = 12; 
const int SIMO = 11; 
const int SCLK  = 13;
const int SPISTE = 7; 
const int SPIDRDY = 2;
volatile int state = LOW;


void afe44xxInit (void);
void afe44xxWrite (uint8_t address, uint32_t data);
uint32_t afe44xxRead (uint8_t address);
signed long average_BPM( signed long );
volatile char DataPacketHeader[6];
volatile char DataPacket[10];
volatile char DataPacketFooter[2];
int datalen = 0x09;
unsigned long time;

volatile static int SPI_RX_Buff_Count = 0;
volatile char *SPI_RX_Buff_Ptr;
volatile int Responsebyte = false;
volatile unsigned int pckt =0, buff=0,t=0;
unsigned long ueegtemp = 0, ueegtemp2 = 0;
unsigned long IRtemp,REDtemp;
signed long seegtemp=0, seegtemp2=0;
volatile int i;


uint16_t aun_ir_buffer[100]; //infrared LED sensor data
uint16_t aun_red_buffer[100];  //red LED sensor data

#define FS            25    //sampling frequency
#define BUFFER_SIZE  (FS*4) 
#define MA4_SIZE  4 // DONOT CHANGE
#define min(x,y) ((x) < (y) ? (x) : (y))

const uint8_t uch_spo2_table[184]={ 95, 95, 95, 96, 96, 96, 97, 97, 97, 97, 97, 98, 98, 98, 98, 98, 99, 99, 99, 99, 
              99, 99, 99, 99, 100, 100, 100, 100, 100, 100, 100, 100, 100, 100, 100, 100, 100, 100, 100, 100, 
              100, 100, 100, 100, 99, 99, 99, 99, 99, 99, 99, 99, 98, 98, 98, 98, 98, 98, 97, 97, 
              97, 97, 96, 96, 96, 96, 95, 95, 95, 94, 94, 94, 93, 93, 93, 92, 92, 92, 91, 91, 
              90, 90, 89, 89, 89, 88, 88, 87, 87, 86, 86, 85, 85, 84, 84, 83, 82, 82, 81, 81, 
              80, 80, 79, 78, 78, 77, 76, 76, 75, 74, 74, 73, 72, 72, 71, 70, 69, 69, 68, 67, 
              66, 66, 65, 64, 63, 62, 62, 61, 60, 59, 58, 57, 56, 56, 55, 54, 53, 52, 51, 50, 
              49, 48, 47, 46, 45, 44, 43, 42, 41, 40, 39, 38, 37, 36, 35, 34, 33, 31, 30, 29, 
              28, 27, 26, 25, 23, 22, 21, 20, 19, 17, 16, 15, 14, 12, 11, 10, 9, 7, 6, 5, 
              3, 2, 1 } ;

static  int32_t an_x[ BUFFER_SIZE]; 
static  int32_t an_y[ BUFFER_SIZE]; 

int32_t n_buffer_count; //data length

int32_t n_spo2;  //SPO2 value
int8_t ch_spo2_valid;  //indicator to show if the SPO2 calculation is valid
int32_t n_heart_rate; //heart rate value
int8_t  ch_hr_valid;  //indicator to show if the heart rate calculation is valid

long status_byte=0;
uint8_t LeadStatus=0;
boolean leadoff_deteted = true;
uint8_t spo2_probe_open = false;
int dec=0;



void setup()
{
   delay(2000) ;   // pause for a moment
   Serial.begin(57600);
   
   SPI.begin(); 
   
   // set the directions
   pinMode (SPISTE,OUTPUT);//Slave Select
   pinMode (SPIDRDY,INPUT);// data ready 
 
   attachInterrupt(0, blink, RISING ); // Digital2 is attached to Data ready pin of AFE is interrupt0 in ARduino

   // set SPI transmission
   SPI.setClockDivider (SPI_CLOCK_DIV8); // set Speed as 2MHz , 16MHz/ClockDiv
   SPI.setDataMode (SPI_MODE0);          //Set SPI mode as 0
   SPI.setBitOrder (MSBFIRST);           //MSB first

// Packet structure
  DataPacketHeader[0] = CES_CMDIF_PKT_START_1;  //packet header1 0x0A
  DataPacketHeader[1] = CES_CMDIF_PKT_START_2;  //packet header2 0xFA
  DataPacketHeader[2] = datalen;                // data length 9
  DataPacketHeader[3] = (uint8_t)(datalen >> 8);
  DataPacketHeader[4] = CES_CMDIF_TYPE_DATA;
  
  DataPacketFooter[0] = 0x00;
  DataPacketFooter[1] = CES_CMDIF_PKT_STOP;

   
   afe44xxInit (); 
}
/////////////////////////////////////////////////////////////////////////////////////////////////////////////////

void loop()
{    
     if (state == HIGH)  
     {
        detachInterrupt(0);
        afe44xxWrite(CONTROL0,0x000001);  
        IRtemp = afe44xxRead(LED1VAL);
        afe44xxWrite(CONTROL0,0x000001);  
        REDtemp = afe44xxRead(LED2VAL);   
        Responsebyte = true;
     }  
                    
  if(Responsebyte == true)
  {
      
      IRtemp = (unsigned long) (IRtemp<<10);
      seegtemp = (signed long) (IRtemp);
      seegtemp = (signed long) (seegtemp>>10);  
                      
      REDtemp = (unsigned long) (REDtemp<<10);
      seegtemp2 = (signed long) (REDtemp);
      seegtemp2 = (signed long) (seegtemp2>>10);
  
      if(dec==20)
      {
        aun_ir_buffer[n_buffer_count]=(uint16_t) (seegtemp>>4);
        aun_red_buffer[n_buffer_count]=(uint16_t) (seegtemp2>>4);
        n_buffer_count++;
        dec=0;
        
      }
      dec++;
  
      if(n_buffer_count>99)
      {
        
        estimate_spo2(aun_ir_buffer, 100, aun_red_buffer, &n_spo2, &ch_spo2_valid); 
       /* if(n_spo2 == -999)
        spo2_probe_open = true;
        else
        spo2_probe_open = false;
       */
      // Serial.println(n_spo2);
        n_buffer_count=0;
      }         

        
      DataPacket[0] = seegtemp;
      DataPacket[1]  = seegtemp>>8;
      DataPacket[2] = seegtemp>>16;
      DataPacket[3] = seegtemp>>24; 
   
      DataPacket[4]  = seegtemp2;
      DataPacket[5] = seegtemp2>>8;
      DataPacket[6] = seegtemp2>>16;
      DataPacket[7] = seegtemp2>>24;

     if(n_spo2 == -999)       
      DataPacket[8] = 0;       
     else
      DataPacket[8] = n_spo2;       

      for(i=0;i<5;i++)
      Serial.write(DataPacketHeader[i]);
                
      for(i=0; i<datalen; i++) // transmit the data
      Serial.write(DataPacket[i]);

      for(i=0; i<2; i++) // transmit the data
      Serial.write(DataPacketFooter[i]);
      
      Responsebyte = false;
      state = LOW;
      attachInterrupt(0, blink, RISING );      
       
  }                   
        
}

///////// Gets Fired on DRDY event/////////////////////////////

void blink()
{
  state = HIGH;
}

////////////////AFE44xx initialization//////////////////////////////////////////
void afe44xxInit (void)
{ 
  //  Serial.println("afe44xx Initialization Starts"); 
     afe44xxWrite(CONTROL0,0x000000);

     afe44xxWrite(CONTROL0,0x000008);  

     afe44xxWrite(TIAGAIN,0x000000); // CF = 5pF, RF = 500kR
     afe44xxWrite(TIA_AMB_GAIN,0x000001); 
     
     afe44xxWrite(LEDCNTRL,0x001414);    
     afe44xxWrite(CONTROL2,0x000000); // LED_RANGE=100mA, LED=50mA 
     afe44xxWrite(CONTROL1,0x010707); // Timers ON, average 3 samples  
    
     afe44xxWrite(PRPCOUNT, 0X001F3F);

    afe44xxWrite(LED2STC, 0X001770); //timer control
    afe44xxWrite(LED2ENDC,0X001F3E); //timer control
    afe44xxWrite(LED2LEDSTC,0X001770); //timer control
    afe44xxWrite(LED2LEDENDC,0X001F3F); //timer control
    afe44xxWrite(ALED2STC, 0X000000); //timer control
    afe44xxWrite(ALED2ENDC, 0X0007CE); //timer control
    afe44xxWrite(LED2CONVST,0X000002); //timer control
    afe44xxWrite(LED2CONVEND, 0X0007CF); //timer control
    afe44xxWrite(ALED2CONVST, 0X0007D2); //timer control
    afe44xxWrite(ALED2CONVEND,0X000F9F); //timer control

    afe44xxWrite(LED1STC, 0X0007D0); //timer control
    afe44xxWrite(LED1ENDC, 0X000F9E); //timer control
    afe44xxWrite(LED1LEDSTC, 0X0007D0); //timer control
    afe44xxWrite(LED1LEDENDC, 0X000F9F); //timer control
    afe44xxWrite(ALED1STC, 0X000FA0); //timer control
    afe44xxWrite(ALED1ENDC, 0X00176E); //timer control
    afe44xxWrite(LED1CONVST, 0X000FA2); //timer control
    afe44xxWrite(LED1CONVEND, 0X00176F); //timer control
    afe44xxWrite(ALED1CONVST, 0X001772); //timer control
    afe44xxWrite(ALED1CONVEND, 0X001F3F); //timer control

    afe44xxWrite(ADCRSTCNT0, 0X000000); //timer control
    afe44xxWrite(ADCRSTENDCT0,0X000000); //timer control
    afe44xxWrite(ADCRSTCNT1, 0X0007D0); //timer control
    afe44xxWrite(ADCRSTENDCT1, 0X0007D0); //timer control
    afe44xxWrite(ADCRSTCNT2, 0X000FA0); //timer control
    afe44xxWrite(ADCRSTENDCT2, 0X000FA0); //timer control
    afe44xxWrite(ADCRSTCNT3, 0X001770); //timer control
    afe44xxWrite(ADCRSTENDCT3, 0X001770);
  
    delay(1000);
   // Serial.println("afe44xx Initialization Done"); 
}

/////////////////////////////////////////////////////////////////////////////////////////////////////////////////
void afe44xxWrite (uint8_t address, uint32_t data)
{
    digitalWrite (SPISTE, LOW); // enable device
    SPI.transfer (address); // send address to device
    SPI.transfer ((data >> 16) & 0xFF); // write top 8 bits
    SPI.transfer ((data >> 8) & 0xFF); // write middle 8 bits
    SPI.transfer (data & 0xFF); // write bottom 8 bits    
    digitalWrite (SPISTE, HIGH); // disable device
}

/////////////////////////////////////////////////////////////////////////////////////////////////////////////////
unsigned long afe44xxRead (uint8_t address)
{       
    unsigned long data=0;
    digitalWrite (SPISTE, LOW); // enable device
    SPI.transfer (address); // send address to device
    //SPI.transfer (data);
    data |= ((unsigned long)SPI.transfer (0)<<16); // read top 8 bits data
    data |= ((unsigned long)SPI.transfer (0)<<8); // read middle 8 bits  data
    data |= SPI.transfer (0); // read bottom 8 bits data
    digitalWrite (SPISTE, HIGH); // disable device
    

    return data; // return with 24 bits of read data
}
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

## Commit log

2015-10-28 Eagle file
    [pc_afe4400_shield.brd, pc_afe4400_shield.sch]
2016-12-29 updated schematic
    [pc_afe4490_shield.brd, pc_afe4490_shield.sch]
2017-01-19 Updated schematics for v2 breakout and shield
    [pc_afe4490_brk_v2.brd, pc_afe4490_brk_v2.sch, pc_afe4490_shield.brd, pc_afe4490_shield.sch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]
2017-01-20 Fixed the j1, j2 use error for supporting Arduino SAMD boards
2018-04-01 Updated Reset pin config in firmware
    Corrected bug in software for RESET pin handling

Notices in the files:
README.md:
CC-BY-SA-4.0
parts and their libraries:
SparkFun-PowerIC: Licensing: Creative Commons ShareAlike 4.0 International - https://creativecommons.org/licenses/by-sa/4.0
